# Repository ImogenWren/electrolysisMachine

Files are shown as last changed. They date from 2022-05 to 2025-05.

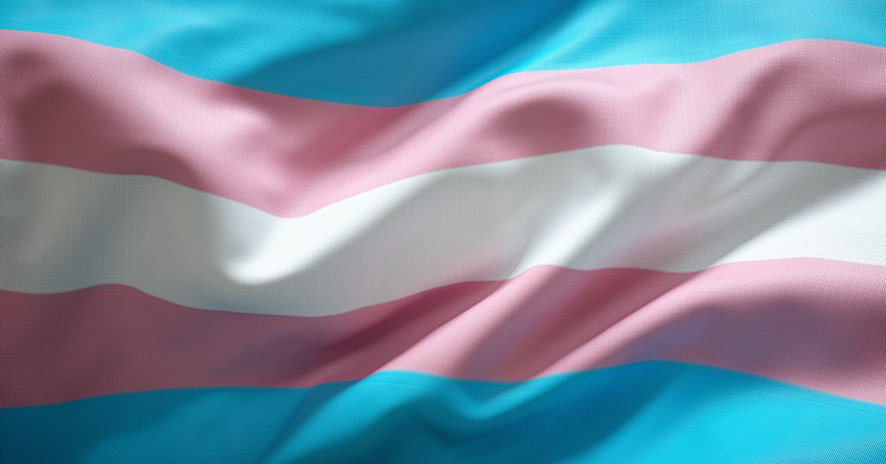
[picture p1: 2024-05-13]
Documentation/TransFlag_AdobeStock_279219643.png

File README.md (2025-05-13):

# electrolysisMachine
 Schematics & Build Plan for DIY Electrolysis Machine for Hair Removal #transhealth

## Contributers
_The following people are thanked for their contribution towards this project_
 - Imogen Wren -> Electronics Lead
 - xxxxxx      -> Power Supply & BMS design

## Notes
_I have just been made aware of someone who is following the origional reddit design, and is quite far into the process with PCBs already in production. Please find a link to this project here: https://hexbear.net/post/2795875_

However I am going to carry on with my design, as I believe my version will be far more useable for those that dont have electronic test equipment to hand.

## System Description
This project is an attempt to build a digitallly controlled version of this DIY Hair Electrolysis machine found on the reddit post [i_built_an_electrolysis_machine_epilator](https://www.reddit.com/r/electronics/comments/8ek9dt/i_built_an_electrolysis_machine_epilator/).
The origional design requires external ampmeters to calibrate, and relies on manually tuning and testing the circuit to ensure settings are correct before delivering current to the hair follical.

To make this project accessable, and build in the ability to add additional safety system, the analog elements should be replaced with digital electronics. The digital electronics should be based around the Arduino Framework to make it as easy as possible for others to build this project.
Once the circuit has been proven, a PCB will be designed to allow others to easy replicate the project.

The hope is to make this a complete open-source, safe, cheap and easy system to build and use, to maximise the impact to the communities that are currently denied access to private hair removal services.

This project is open-source and welcomes collaborators on everything from project goals, design, production and testing!

NOTE: _This is an attempt to design a medical product to deliver current through a paitents skin, within in an open source framework.
Any attempt to follow the designs or guides within this repo are undertaken ENTIRELY at the users own risk._ 

## Design Goals
- [G1] Safe & Consistant operation of a constant current source, able to deliver up to 2.0 mA in pulses of up to 10s between probes attached to users skin.
- [G2] Current Source should be controllable down to 0.0 mA, with a resolution of at least 0.2 mA and accuracy of +-0.2 mA. (Exact values to be reviewed)
- Timer pulse should be controllable down to 1.0 mS, with a resolution of at least 0.5 mS, and accuracy of +-0.2 mS. (Exact values to be reviewed)
- 0-2 mA current to voltage sensor with a resolution of at least 0.2 mA and accuracy of +-0.2 mA (Exact values to be reviewed)
- Operation from 3S or less LiPo battery pack. (Can be reviewed and voltage increased if nessissary to achieve other design goals)
- Battery Management System (BMS) with USB-C (If 5V is sufficient to charge) AND 2.1mm DC jack (or similar generic connector) included.
- Passive Safety system to cut power if 2.0 +-0.2 mA is exceeded.
- Passive safety system to cut power if 10s pulse time is exceeded.
- Microcontroller will be AtMega328p OR Arduino Nano Dev board for ease of replication. 
- Simple to operate user interface:
 - Large display for SET_CURRENT, PULSE_TIME.
 - Settings menu to change MAX_CURRENT, MAX_PULSELENGTH
 - 1x Rotary Encoder with button for user inputs.
 - 1x TRIGGER button
 - 1x CANCEL button
 - Save at least 3x User profiles for quick settings changes
- 3D printable case to contain both electronics, battery system and probes.
- Clear & Simple Build Manual
- Clear & Simple operation instructions (Will need to collaborate to ensure clear communication of medical information)

### Strech Goals
- 3D printable case to include hygenic supplies required for safe operation.
- Chargeable on 5V USB, or 12V power.

## Project Steps:
_These steps are each created with the intent of de-risking the project as quickly as possible,
by focusing on small functional prototypes that can be intergrated at the earliest opportunity,
avoiding increasing complexity untill individual sub-systems are proven._

1. Model voltage controlled, 0-2mA constant current driver in LTspice. [x]
 - 1b. Model Power Supply [x]
2. Construct Current source prototype & Test. [x]
   - 2b. Construct and test power supply. [x]
3. Model 0-2 mA current to 0-5 V sensing circuit in LTspice. []
4. Construct current sensor prototype & test. []
5. Integrate current sensor with Arduino controller and test ability to meet sensitivity requirements. []
6. Integrade constant current driver with Arduino controller, including manual (pot) controls, and test accuracy of output pulse against requirements. [] <br>
- 6b. Create Alpha Version firmware for manual operation of the PULSE_OUTPUT  [] 
7. Model circuit protection concepts in LTspice. []
8. Integrate passive circuit protection to existing prototypes (if possible) and test against requirements.[]
9. Integrate User Interface with existing prototypes and test function of dsiplay & all input devices. []
10. Finalise schematic & Design PCB [] <br>
- 10b. Start design of 3D printed enclosure, to coencide with PCB design (Though should not block PCB design or production) []
11. Develop Beta version firmware including Functional user interface. []
12. Build Production prototype. []
13. Test Beta Firmware with Production prototype. []
14. Release Verified V1.0.0 PCB design & Make PCBs available to purchase. []
15. Release production Firmware. []
16. Develop "DIY Kit" Including build & user guides. []

## Design: Schematic
_The schematic is the most up to date & tested version of each sub system_

### Power Supply
This circuit has been tested with a 12v power supply, driven from a microcontroller. Duty cycle did not affect voltage generated untill the extremes.
Tested using microcontroller for PWM signal, finished version will be driven by 555 timer. <br>

- Use LM317 to regulate to 30v (https://www.homemade-circuits.com/how-to-build-simplest-variable-power/) NOTE: This could maybe be used as current source
- 
- 



<br>
555 Circuit Values:
- R1: 100k
- R2: 1.5k (sets frequency to 48kHz)
- C1: 10n (sets frequency to 48kHz)

Breadboarded & tested, can deliver 2.09 mA @ 32v, unloaded maxV = 45

## December 2024 Research -> Current Controller
- https://forum.arduino.cc/t/precision-current-control-and-measurment/282352
- https://www.allaboutcircuits.com/textbook/semiconductors/chpt-8/voltage-to-current-signal-conversion/

## Circuit 3: Transconductance Amplifier

- Modelled correctly and is even simpler than previous topologies
- Tested & working with 358C Op-Amp

- Layouyt:
- 

- Mrs Signal Layout


## December 2024 Research -> Current Measure:
- https://www.adafruit.com/product/904
  - "A precision amplifier measures the voltage across the 0.1 ohm, 1% sense resistor. Since the amplifier maximum input difference is ±320mV this means it can measure up to ±3.2 Amps. With the internal 12 bit ADC, the resolution at ±3.2A range is 0.8mA. With the internal gain set at the minimum of div8, the max current is ±400mA and the resolution is 0.1mA"
------------------------------------------------------------------------
>
>

# State-of-the-Art

### Description of the Existing Reddit Design

_It's battery powered. epilator circuit runs off 3 9v batteries in series, ammeter and voltmeter run off a separate supply, from a usb battery pack. 
Device delivers a voltage thats adjustable from 6v to 22v. Current sink (at probe) is adjustable from 0mA to 2mA. 
Supply is run through ecg electrode which is placed right next to the site I'm working on. A 555 timer is used to pulse the current sink. 
I'm using professional electrolysis probes, F4 shank stainless steel. Probe housing is made from a d-sub female crimp pin soldered
to a wire and covered with a piece of heat shrink tubing. (F4 size probe fits snug into the socket)._
(abbxrdy, 2018) Accessed: (Reddit 2022)

## Existing System Use Guide

_To adjust current sink, toggle the test switch an turn the current knob, the value is displayed on the ammeter. To use, slide the test switch back. When the probe is inserted, you hit the trigger button and it delivers the current for a specified time. You can see how much it's sinking. If it's sinking less than what it was set for you can increase the voltage to overcome the resistance between the probe and the electrode. The setting that I use is 0.5mA at 15v. This will kill a pubic hair in 10 seconds without much discomfort if the probe is correctly inserted into the hair follicle.
For more information on what size probes to use for what hairs, and how much current to deliver over whatever time period you can search for a "units of lye" chart_

#### Exposure Requirements

_for me, the settings I'm using are 15 volts with 0.5mA sink. This setting treats a pubic hair in 10-15 seconds when needle is placed properly. It just slides right out._

## Needles & Additional Items Required

https://www.texaselectrolysissupply.com/

Ballet brand, f shank, size 4

### Future Improvements for Reddit Version

_second revision of this thing with a lot more safety considerations. The current source will be galvanically isolated from the main supply and have an adjustable current source configurable from 0mA to 2mA and a fixed current sink set at 2mA. The trigger circuit will use an opto isolator and there will be a current monitor on the isolated area that passes it's reading outside through an iso op amp. If the probe sinks more than 2mA the machine will shut down._

# Personal Thoughts and Reflection

## TODO:
- Replace 555 with microcontroller

## Current Schematic
electrolysisMachine_Schematic_source

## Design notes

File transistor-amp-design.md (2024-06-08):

# Transistor Amplifyer Design
Source Used: https://www.circuitbasics.com/transistor-amplifiers/

This is mostly copied verbatium for now, will go through calculations for my own purposes later:

How the circuit works

Our design begins with a look inside the transistor itself.


_In the emitter, there is a ‘hidden’ resistor Re. You can’t measure it with a multimeter, but it’s there. Re has a dynamic value dependent on the collector current Ic such that Re = 25/Ic,
 where Ic is in mA. So if Ic is 10mA, then Re = 2.5Ω. The other important thing to know is that the transistor’s current gain can be approximated as Ic/Ib and is called hfe. Typically, 
50 to 1000 for small transistors. The transistor choice in this design is not an issue; almost any small signal NPN type will be fine._

_For any transistor to work, it needs to be biased. This means that the base is raised or biased 0.6V higher than the emitter.
Besides that, we also need to think about signal headroom and input impedance. 
Any voltage that we set up on the input is going to affect the voltage at the output. 
The voltage at the output is a DC offset, and we want to make this work in our favor. 
The choice of the collector resistor and the current through it will govern this._

_The first assumption is what this circuit will be driving—what output resistance must it have.
We should have an output resistance at least 2x to 5x lower than the next stage. 
So let’s assume the next stage input resistance will be 47k and make our output resistance 10k. 
We do this simply by making R110k (this is a bit of a simplification but is close enough)._

_The next assumption is that we don’t want a distorted output where one of the half-cycles clips.
We want to set the collector voltage of Q1 to be half-way. So if R1 is 10k and the voltage across 
it is 12/2, i.e., 6V, the current through R1 is V/R = 6/10000 = 0.6mA. This is our collector current,
and we can now find re=25/Ic = 42Ω. We will use this later._

_For stability and good biasing, we would like the emitter of Q1 to be at about 1V. This will allow a 
reasonable signal swing at the base of Q1. So to get 1V across R2 knowing the current through it is 0.6mA,
R2 = V/I = 1/0.6 = 1.6k, let’s make it 1k5. This will change the voltage on the emitter slightly so V=IR = 0.6* 1500 = 0.9V._

_Now, the voltage on the base will ALWAYS be 0.6 higher than the emitter, and the current into the emitter will be Icollector/hfe. 
The datasheet for the BC337 shows an hfe of 600. Let’s assume a bit less to be safe, say 200. So Ibase is 0.6/200 =0.003mA.
For stability, we will make the current flowing down the divider chain R3, R4 ten times bigger, i.e., 0.03mA, so the voltage 
across R4 is 0.9 + 0.6 = 1.5 and the current through is 0.03, R4 = V/I = 1.5/0.03 = 50k. We make it a standard value of 47k. 
This slightly changes the current to 1.5/47k = 0.032mA. R3 has 12V on one end and 1.5 on the other. The voltage across it becomes
12-1.5 = 10.5V, and so R3 = V/I = 10.5/0.032 = 328k. Make it a standard value of 330k. R5 has nothing to do with the transistor design. 
It provides a voltage to supply the electret mic (it has an electrostatic capacitor coupled to a small FET inside), and 10k is a usual value._

_Now, how much gain can we expect? The gain will be R1/R2+re = 10k/ 1k5+42 =6.48. This is not that useful, but we can increase this
by AC bypassing R2 with a capacitor C3 leaving only re. The DC conditions remain the same, but the gain is now 1500/42 = 35.
We must make C3 with a value such that its reactance is equal to R2 at our lowest frequency, 40Hz, so C3 = 1/2πfXc = 2.6uF.
Hence, make it 10uF._

_The remaining design is for the input and output capacitors. C1 is easy. The input resistance is a combination of R3 in parallel with
R4 in parallel with
R2+re*hfe, (1k5+42)*200 = 300k._

_It is pretty much just a bit less than R4, say 40k, but it needs to have a capacitive reactance equal to R4 at the lowest 
frequency we intend to amplify. If we choose 40Hz Xc = 1/(2πfC), then C = 1/2πfXc = 0.39uF. In the same way,
C2 = 1/2π40*10k = 0.4uF. Hence, make it 1uF._

_The next step in our design is to add a buffer transistor to increase the output drive capacity to enable a small
(high impedance) speaker. This is called an emitter follower. It has no voltage gain, but it has a much lower output impedance.
We will also provide some DC negative feedback to ‘lock’ the bias of Q1._

The only components that are going to change are R3 and C4; C2 has been replaced with C4. Without C4, there would be a DC offset across the speaker.
We need to know what the impedance of the load is, i.e., the speaker. This simple circuit cannot drive an 8Ω speaker; you would need a power amplifier for that.
Assuming we are using a cell phone earbud at about 100Ω. For a 12V pp swing that would be about 1W, which is pushing it for this simple circuit, 
the emitter follower’s static DC power should be equal to that to result in 100mA in the transistor, which is way beyond its means.
We are going to back off our expectations and allow a maximum of 10mA in Q2. As Q2 emitter is 6-0.6V = 5.4V then R6=5.4/0.01 = 540, 
call it 560Ω. R3 is now no longer connected to 12V, but to 6V, its value becomes (6-1.5)/0.03 = 150K. C4 is now 1/2π40*100 = 25uF.

amplifier_3-1080x877

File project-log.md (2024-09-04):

# project-log: Electrolysis Machine
_Project log showing complete development notes_
## Step 1: Model Voltage Controlled Current Source
- Current Servo, Voltage Controlled Current Source
 Op-Amp-Voltage-Controlled-Current-Source-Circuit-Diagram
"The third requirement is the shunt resistor. Let's stick into 1ohms 2watt resistor. Additional two resistors are required, one for the MOSFET gate resistor and the other one is the feedback resistor. These two are required for reducing the loading effect. However, the drop between these two resistors is negligible.

Now, we need a power source, it is a bench power supply. There are two channels available in the bench power supply. One of them, the first channel is used to provide power to the Circuit and the other one which is the second channel used to provide the variable voltage to control the source current of the circuit. As the control voltage is applied from an external source, both channels need to be in the same potential, thus the ground terminal of the second channel is connected across the first channel ground terminal."

### LTspice modelling
Most linear response found. Will work with 3v3 logic



Increasing voltage to 27 to match origional (3x 9v)
Commands Used:
- `.dc V2 0 5 0.1`
- Now shows almost linear response across the entire control voltage range


Testing current setpoint given change in R3 (sweep from 0R to 10M)
Commands used:
- `.step param R3 list 0R 1R 10R 100R 1K 10k 100k 1000k 10000k`
- `.op`
- Shows constant current through changing load


### Calculating DAC Resolution (10 bit)
- ADC max val = 1023
- Max Current output = 2.36 mA
- Max Current / Max ADC = 0.00231 mA per ADC
- Resolution of 0.002 mA is possible using Arduino ADC, though slight non-liniarity at the lowest control voltage
- MEETS DESIGN GOAL [G2] Resolution of 0.2mA

(Source - [eee-calculator](https://github.com/PanGalacticTech/engineering-calculator-2023)

### Accounting for PWM
As the control voltage from the microcontroller will be PWM, rather than a descrete voltage, this should be added to the simulation. This may not matter, as average current delivered will be the same, however in the origional design the current supplied was constant, not pulsed and I wish to at least attempt to replicate that. A decision can be made later which outcome is better, though this might require testing which will be hard to quantify if I am the only test subject.

### Origional Design modelling PWM control voltage
Arduino nano PWM frequency = 490.2 (this can be changed but why change if not required)
Period = 1/490.2 = 2.04 mS 
Model PWM frequency at 2 mS period, with 50% Duty
Using Commands: 
`.tran 0 1 0 0.1 startup` // DC Transfer for 1 second after startup <br>
`**PULSE(0 5 0 0 0 1m 2m 0)**` // Pulse voltage source <br>
` step param R3 list 0R 1R 10R 100R 1K 10k 100k 1000k 10000k` // step R3 to show constant current regardsless of load <br>

This shows that the output will also be pulsed, the first attempt to remove this pulse will be the addition of a capacitor to the control voltage. Placed after the 100k resistor, this will form a low pass filter, for which the cutoff frequency must be pushed as low as possible to block all but DC.

Selecting 
> capacitor: 1 uF = cutoff_frequency: 1.59 Hz
> capacitor: 10 uF = cutoff_frequency: 0.16 Hz
> 
 Modelling with 1uF capacitor as these are cheaper and easier to source without going to electrolytic.
Using Commands: 
`.tran 0 1 0 0.1 startup` // DC Transfer for 1 second after startup <br>
`**PULSE(0 5 0 0 0 1m 2m 0)**` // Pulse voltage source <br>
` step param R3 list 0R 1R 10R 100R 1K 10k 100k 1000k 10000k` // step R3 to show constant current regardsless of load <br>

Tested with a few different C1 values, nothing showed significant DC smoothing untill 100 uF, shown below:

DC Voltage Ripple:

DC Current Ripple: 1.30 - 1.18 = 12 mA

Next try modelling with smaller value capacitors in paralellel



DC Current Ripple: 1.30 - 1.18 = 12 mA

NO change!
 100uF is likely optimal for this purpose, though introduces a slower current rise & fall time. 

### Testing capacative filter on output of OP-AMP to mosfet
Now lowpass filter with 10k, 

100uF = 0.16 cutoff frequency


Ramp takes over half a second to reach full power, this may assit in reducing pain or shock, or may prolong pain. Certainly will not be suitable for cutting power to probe.



At 1u, ramp up is only 60mS, current ripple of: 1.26 - 1.224 = 0.036mA ripple this is very acceptable. Wave has also been smoothed to sinusoildal. Could this have an effect on pain?


## Step 1b: Model The Power Supply

_The power supply needs to be capable of providing the correct current considering all of the possible loads that a paitents skin could offer._
In order to specify the full requirements for the power supply, we could take data of different peoples skin resistivity, calculate averages, min & max, however. For the first prototypes we will bypass this, and attempt to replicate the power supply used in the origional project. 

This comprised of 3x 9v batteries, or 27v rail-to-rail.

For this implementation we wish to achieve this from a single 12v power supply at most, as these are the most common available. For this we could use a charge pump.

_For previous, failed attempts at specifying the power supply circuit, see the additional file `step-1b-charge-pump-circuits.md`_ <br>

### Attempt 2: 555 based charge pump
_The initial modelling using a charge pump IC with a +18 and -9v output seemed to be a dead end, so next we will try to model a 555 based charge pump with an output of ~+30v_

This next attempt will use this basic building block: <br>

(circuits-diy.com)


https://www.circuits-diy.com/charge-pump-circuit-getting-higher-voltage-from-low-voltage-source/

We could potentially use the microcontroller itself to provide the PWM for the charge pump, this may be explored later, but first we will keep things as simple as possible and model with a 555 timer. For the 555 circuit, I will be adapting a circuit origionally designed for a high voltage SMPS for use with Nixie Tubes, documented here:
https://pangalactictech.com/12v-dc-to-300v-dc-smps/


NE555 Working Voltage: 4.5-16v, fits perfectly with the 12v supply voltage specification.

#### Modelling Charge Pump
_Initial Results Promising_


stable 36v output given 12v input

next test CV frequency sweep - cant set up correctly

Tested at different CV, rise time differed but max V output did not

Then test with varying loads

tested with additionally diode stage and suitable load:


going to try adding one more diode stage

 Peak voltage of ~30v, capable of just over 30mA of current, 

Decreased R8 t0 4k7, increased frequency to 114 KHz

## Simulating pulse in LTspice
_Finally learned to set waveform using frequency & duty cycle_

At duty cycle of:
0.2 = 21.3v output
other duty cycles no difference

but lower input v of 5v = lower output voltage. need additional diode stage or higher PWM voltage
   
### Current of PWM Signal
I decided to check the current required to deliver the simulations shown above, during inrush

- First looking at inrush current:
- -
- ~100 A

- Then looking at each pulse as steady state is reached:
- 
- Still pulling about 2.5 A

This is absolutly not suitable, microcontroller pins can source about 20-40mA at max. For longevity, we wil try and keep it to about 20 mA

- R = V/I
- R = 5/0.020 = 250 ohm
- So lets put a series resistor in the PWM path to limit the current to this value

-Current limited to 18mA BUT Vout now limited to 11.5 v
- 

- So PWm needs to be amplified, simple transistor will do or does this charge pump approach have a fundemental flaw?

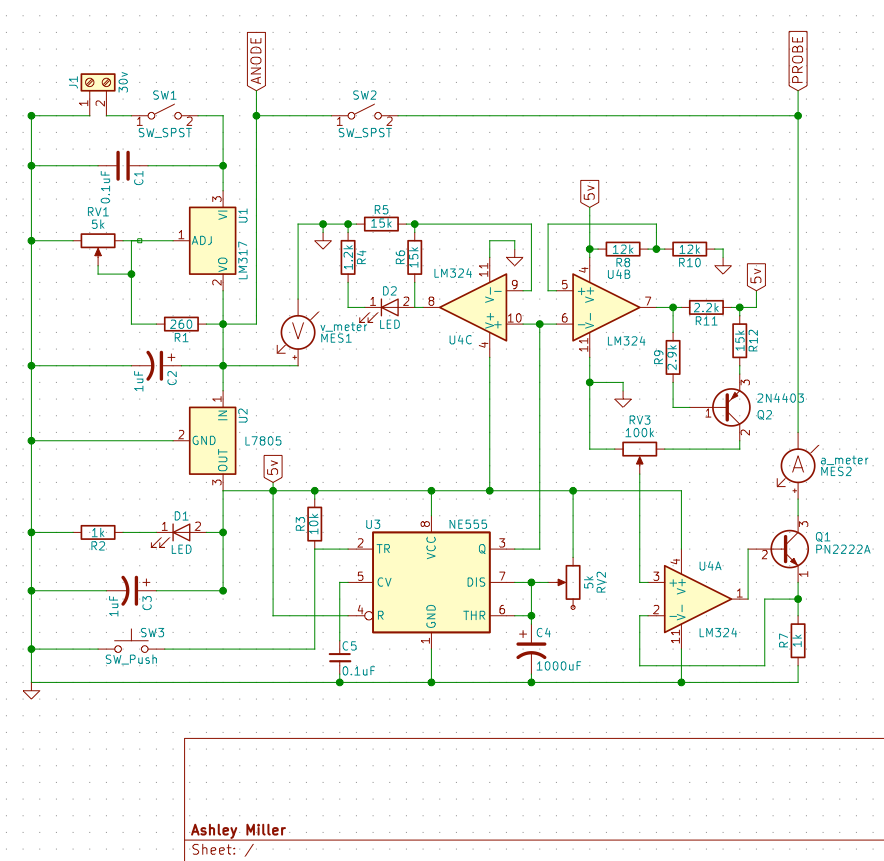
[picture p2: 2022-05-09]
Documentation/electrolysisMachine_Schematic_source.png

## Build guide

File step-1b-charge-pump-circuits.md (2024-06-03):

# Step 1 - Modelling a charge pump circuit
_Moving exploration done on virtual grounds here as it ended up being a dead end in the development tree_

### Attempt 1: Charge Pump IC

The Charge pump selected is based on the Klon charge pump, which delivers a +18v and -9v output, provided a 9v input, and is based on a readily available ILC7660S Charge pump IC. It can also handle voltages up to 12v, given extensive testing (although this may be slightly out of spec and not reccomended) It does offer an opporunity to regulate a 12v input voltage down to 9v to feed the charge pump a very consistant input voltage.

### Schematic


### Issues with Charge Pump
- Unable to model circuit I have experience with as cannot find a model for ILC7660S or TL1044 IC
- In order to get the full 27v rail-to-rail voltage, the negative rail must be used as a virtual ground for the skin probe.
For this reason, I am not going to worry about modelling the charge pump, I know this circuit is cabable of outputting these voltages, however we must ensure that
we can modify the current servo implementation to account for the virtual ground, if this is even possible to do.

## First modelling with -9v virtual ground
- Note: To get this to run needed to use fixed power supply set to +9v, with positive rail grounded

- Showed no current controlability, but current output of ~1.7mA
- After boosting Vsupply to 18v (as if from charge pump) Then current output is able to deliver 2.2mA but still uncontrolled.

## Next trying different groundings (virtual/real)
- Ensure ap-amp is bipolar
- added protection diode to Vcontrol to protect microcontroller from negative voltages

Best option found so far using virtual grounds:



Not great: Controllable down to  ~0.65mA and up to ~1.8mA, must be able to go to 0.0 mA

## Trying to find best feedback resistor.
Used commands: <br>
- `.param Rval=0`
- `.step dec param Rval 0 100k 500` (Logarythmic step Rval
- Put `{Rval` in value to sweep



_Not quite sure what this graph is telling me, trying to expand the range available both up and down._
Immediate conclusions: 
- R1 should be less than 68k to avoid limiting current early.
- Run simulation with lower Vcontrol & compare.
- At Vcontrol = 2.5, current should be ~1.1 mA



- Actual results:
   - For any given feedback resistor value, current is above 1.25
   - Best guess from graph would require a 100k resistor but leaning towards 68k
 
- Arse

- Run again with Vcontrol=0v, should be 0mA
- At 100k, current is still 0.6mA

- I think 68k should be selected, then test R4 step value
- Step change R4 made no difference.
- Setting back to 10k
- try stepping R6 - currently 100k with R5 voltage divider 47r to GND
- INTERESTING RESULT:

### Playing around with voltage divider
_I like using a bigger resistor to GND if possible, so try increasing R6 to reduce control voltage
 
This shows 0.0 mA reached at 220k input resistor. Will set to here then check upper Vcontrol output

max output is now only ~0.55 mA
- Try increasing R5
-  Must be above 120 to prevent limiting current. Very sensitive



## Its nae goood



_Might have to think a little harder about whats happening in the circuit_

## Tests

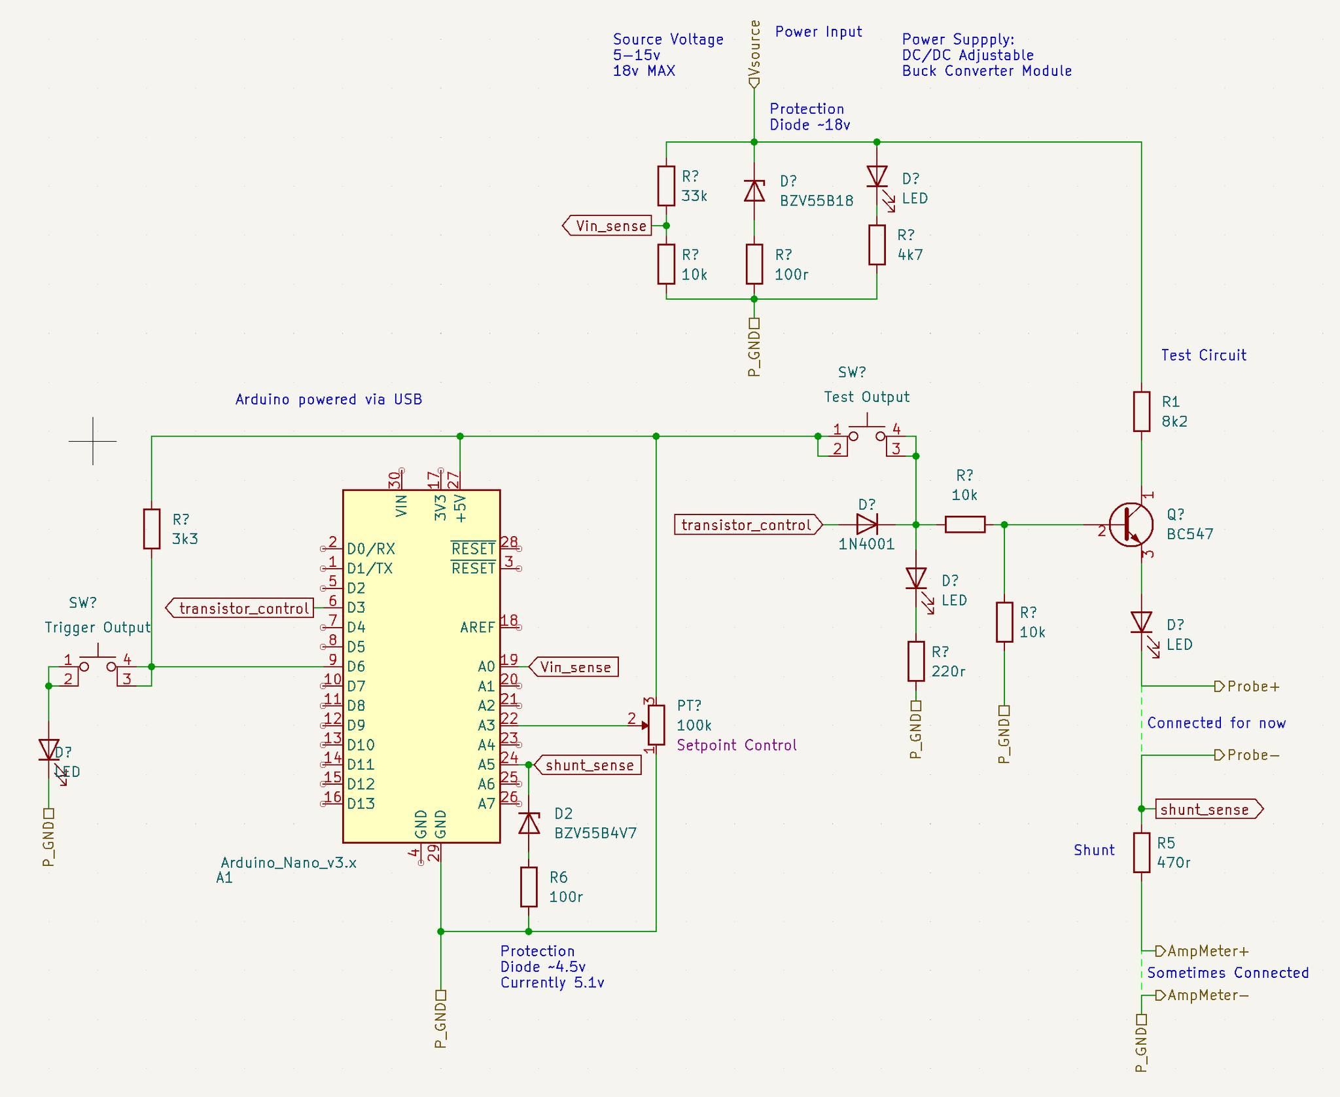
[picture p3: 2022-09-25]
Documentation/Test Circuit Schematic.jpg

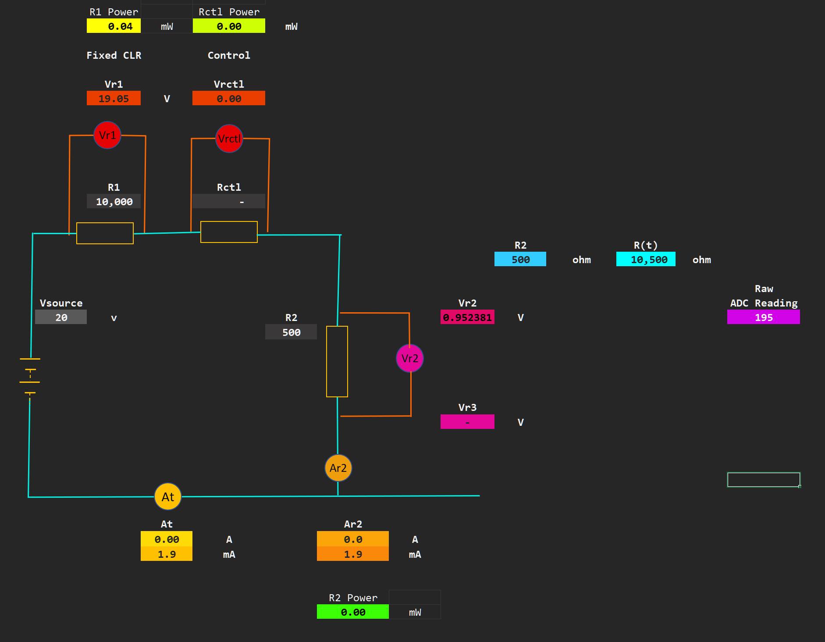
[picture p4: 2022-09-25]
Documentation/Test Circuit Calcs.jpg

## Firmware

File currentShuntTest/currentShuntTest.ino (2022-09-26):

/*
    Test Program for testing current detection using shunt resistor


*/



/* Circuit Specifications:

    Vin <= 20v

    Fixed Resistor = 8k2
    Current Set Resistor = 100-500k
    Shunt Resistor = 500r

    A5 = I measure

    Voltage Divider for Vin Voltage Measurement:
    R1 =  33k
    R2 = 10k

    A7 = Vin Measure


    Circuit Protection:

   15v zener diode with 100r resistor between Vin and GNDs. Clamps Vin to 15v for testing
   5.1v zener diode with 100r resistor between Isense pin and GND. Clamps Detection voltage to <=5v


   Expected Values:

   A5 ADC     =   19    - 195
   A5 Voltage =   0.09  -   0.952
   A5 Current =   0.2   -   1.9

   A7 ADC = 238 - 953
   A7 Voltage = 1.16 - 953
   Vin Voltage = 5 - 20v

*/




#define VIN_SAMPLE_PIN A7
#define SHUNT_SAMPLE_PIN A4

#include <autoDelay.h>
#include <buttonObject.h>



autoDelay sampleDelay;
autoDelay printDelay;
autoDelay inputDelay;
autoDelay outputDelay;

#include "returnStrings.h"


uint16_t u_Vin_ADC;            // Value returned from ACD
float f_Vin_sampled;          // Actual measured voltage
float f_Vin_scaled;           // True Vin Voltage (scaled)


char cs_Vin_sample[20];   // Measured voltage as a char string
char cs_Vin_scaled[20];          // True Scaled voltage as char string

#define ADC_MAX 5.0   // Max voltage for ADC 

#define VIN_ADC_MAX 960
#define VIN_ADC_MIN 0

#define VIN_SAMPLE_MIN 1.16
#define VIN_SAMPLE_MAX 15.0

uint16_t u_shuntADC;               // Value returned from ADC
float f_shunt_Vdrop;            // Measured voltage drop across shunt resistor
float f_shuntI;              // Calculated current through shunt resistor
int16_t shuntI_uA;           // Calculated current in micro amps

#define SHUNT_RESISTOR 500.0   // Shunt resistance in ohms
#define SHUNT_SAMPLE_GAIN 1.0  // gain factor of shunt voltage sampling
#define SHUNT_CURRENT_OFFSET -0.01


char cs_shunt_Vdrop[20];          // Measured voltage drop as char string
char cs_shuntI[20];          // Calculated current as char string


char printBuffer[64];   // buffer to hold all printable values

float voltsPerADC = 0.01;


/* Measured Values & Calibration

    Vin = 5.010   Vin Sampled voltage = 1.18
    Vin = 9.00    Vin Sampled Voltage = 2.065
    Vin = 15.00   Vin Sampled Voltage = 3.448
    15/3.5 = 4.2857
    Therefore
*/

#define VIN_SCALER 4.3
#define VIN_ADC_OFFSET_HIGH -0.20   // offset value between true voltage and calculated voltage at Vmax (15v)
#define VIN_ADC_OFFSET_LOW -0.05      // offset value between true voltage and calculated voltage at Vmin (5v)
float vin_ADV_offset = 0;         // calculated average during setup



/* Adding code for trigger button input
    current set pot input, and
    transistor control output

    At the moment no feedback control, trigger pin sets transistor output high
    Current set pot is read then scaled to mA value but this value is not used yet

*/

#define CONTROL_POT_PIN A0
#define TRIGGER_INPUT_PIN 7
#define TRANSISTOR_OUTPUT_PIN 3
#define INDICATOR_PIN 9   // Mirrors output pin for LED indicator or other indication method
uint16_t controlPotValue;
uint16_t uA_setpoint;

buttonObject button(TRIGGER_INPUT_PIN, BUTTON_PULL_HIGH);    // Set up instance of buttonObject. Pass Button Pin & whether it pulls HIGH, or LOW when pressed.

/*
    PID controller functions

    PID controller will control the current through the shunt resistor using PWM

    pidController library will be used for maths


*/

#include <pidController.h>

#define P_GAIN 1.0
#define I_GAIN 0.0
#define D_GAIN 0.0

pidController PID;

void setupPID() {
  PID.begin();
  PID.updateGain(P_GAIN, I_GAIN, D_GAIN);
}


void setupDigitalPins() {
  pinMode(TRIGGER_INPUT_PIN, INPUT);
  pinMode(TRANSISTOR_OUTPUT_PIN, OUTPUT);
}

void updateOutput(uint8_t output_value) {
  analogWrite(TRANSISTOR_OUTPUT_PIN, output_value);
  analogWrite(INDICATOR_PIN, output_value);    // Mirror output for easy indication
}

void checkButton() {
  //  button.buttonLoop();
  digitalWrite(TRANSISTOR_OUTPUT_PIN, button.detectButton());
}

void controlPot() {
  controlPotValue = analogRead(CONTROL_POT_PIN);   // Sample the ADC
  // This then needs to be scaled to 0 to 2ma. Instead going to scale from 0 to 2000uA to avoid floats
  uA_setpoint = map(controlPotValue, 0, 1024, 0, 2000);
  Serial.print("uA setpoint: ");
  Serial.print(uA_setpoint);
  Serial.print(" uA  |");

}

void setupVinConversions() {
  voltsPerADC = ADC_MAX / 1024.0;
  Serial.print("Volts Per ADC: ");
  Serial.println(voltsPerADC, 6);
  vin_ADV_offset = (VIN_ADC_OFFSET_HIGH + VIN_ADC_OFFSET_LOW) / 2;
  Serial.print("Vin ADC Offset: ");
  Serial.println(vin_ADV_offset, 6);

}

void setupCurrentConversions() {

}


void sampleADCs() {
  u_Vin_ADC = analogRead(VIN_SAMPLE_PIN);
  u_shuntADC = analogRead(SHUNT_SAMPLE_PIN);
  //  Serial.print("Vin ADC: ");
  //  Serial.print(u_Vin_ADC);
  // Serial.print("Shunt ADC: ");
  //Serial.print(u_shuntADC);
}





void calcVin() {
  f_Vin_sampled = u_Vin_ADC * voltsPerADC;
  f_Vin_scaled = (f_Vin_sampled * VIN_SCALER) + vin_ADV_offset;
  //  Serial.print("  Vin Sample: ");
  //  Serial.print(f_Vin_sampled);
  Serial.print("  Vin Scaled: ");
  Serial.print(f_Vin_scaled);
  Serial.print(" |");
}


void calcShunt() {
  f_shunt_Vdrop = u_shuntADC * voltsPerADC;            // Measured voltage drop across shunt resistor
  f_shuntI = ((f_shunt_Vdrop / SHUNT_RESISTOR) * 1000) + SHUNT_CURRENT_OFFSET;
  shuntI_uA = int(f_shuntI * 1000);
  Serial.print(" Shunt Vdrop: ");
  Serial.print(f_shunt_Vdrop);
  Serial.print(" Shunt Current: ");
  Serial.print(f_shuntI);
  Serial.print(" mA, ");
  Serial.print(shuntI_uA);
  Serial.print(" uA");
}



void printOut() {
  // char buffer[64];
  // sprintf(buffer, "%i, %i, %i ,%i, %i, %i", Vin_ADC, Vin_V_Sampled, Vin_Voltage, I_ADC, shunt_Voltage_Drop, I_Current );
}


float testValue = -96.12345;


void setup() {
  Serial.begin(115200);
  setupVinConversions();
  setupDigitalPins();
  setupPID();
}


void loop() {


  // Input Functions
  // Check the PID Controller Settings and State
  if (inputDelay.millisDelay(PID.g_input_delay_mS)) {
    controlPot();
    PID.updateSetpoint(uA_setpoint);
  }

  if (sampleDelay.microsDelay(PID.g_sample_delay_uS)) {
    sampleADCs();
    calcVin();
    calcShunt();
    checkButton();
    PID.updateInput(shuntI_uA);
    Serial.println(" ");
  }
  // Physical Output
  if (outputDelay.microsDelay(PID.g_output_delay_uS)) {
    PID.g_output_value = PID.PIDcontroller(PID.g_setpoint, PID.g_sensor_value, PID.g_output_value);
    //  error_value = PID.g_setpoint - PID.g_sensor_value;
    // average.addDataPoint(error_value);
    // average_error = average.calcMean();
    updateOutput(PID.g_output_value);
  }


 
  //delay(200);

}

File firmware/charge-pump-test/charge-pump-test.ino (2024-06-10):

/* Electrolysis Machine - Charge Pump Driver Test


  Functions:
  - Pot read to PWM duty cycle
  - PWM output to charge pump
  - Voltage meter for output of charge pump


  Circuit:
  - PWM output goes to NOT gate to produce !PWM signal. 
  - PWM & !PWM to 555 Bistable Timer to produce large voltage swing from Vsuppply
  - Charge Pump Circuit driven from 555 output & Vsupply

*/

#define PWM_PUMP_PIN 3
#define POT_PIN A1

#include <autoDelay.h>

autoDelay printDelay;
#define PRINT_DELAY_mS 1000

// Voltmeter Variables
#define VOLTAGE_SENSE_PIN A4
#define V_MAX 30       // Max voltage to measure
#define VMAX_BUFFER 2  // buffer zone to avoid damage
#define V_ADC 5        // Voltage of the ADC
#define R_ONE 10000    // Resistor from Vin
// Next values must be calculated
#define R_TWO 1500                      // Resister to GND calculated by: R_TWO = R_ONE/((V_MAX+VMAX_BUFFER)/V_ADC)
#define ADC_MAX_V 4.8                   // calculated by ADC_MAX_V = (V_MAX+VMAX_BUFFER)/(R_ONE/R_TWO)
#define ADC_TICKS 1024                  // Calculated from 10 bit ADC
#define VOLTMETER_CURRENT_mA 2.67       //mA   // calculated from I = (V_MAX / (R_ONE + R_TWO))*1000
#define ADC_TO_MEAS_V_SCALER 0.00469    // Calculated as    (ADC_MAX_V/ADC_TICKS)
#define ADC_TO_SOURCE_V_SCALER 0.03125  // Calculated as    (ADC_MAX_V/ADC_TICKS)*(R_ONE/R_TWO)
#define MEAS_V_TO_SOURCE_V_SCALER 6.6   // Calculated as (V_meas * (R_ONE/R_TWO))

float V_meas = 1.4;
float V_source = 9.3;


void calculate_voltage_divider() {
}

void sampleVoltage() {
  int adcRead = analogRead(VOLTAGE_SENSE_PIN);
  V_meas = adcRead * ADC_TO_MEAS_V_SCALER;
  V_source = adcRead * ADC_TO_SOURCE_V_SCALER;
}

void setup() {
  Serial.begin(115200);
  Serial.println("\nCharge Pump Test - Prototype\n");
  TCCR1B = TCCR1B & B11111000 | B00000001;  // for PWM frequency of 31372.55 Hz
  pinMode(PWM_PUMP_PIN, OUTPUT);
  analogWrite(PWM_PUMP_PIN, 0);
}

int potRead;
int dutyPercent;
int pwmValue;
int pot_to_pwm() {
  potRead = analogRead(POT_PIN);
  dutyPercent = potRead / 10.23;
  pwmValue = map(dutyPercent, 0, 100, 0, 255);
  return pwmValue;
}

void print_stats() {
  if (printDelay.millisDelay(PRINT_DELAY_mS)) {
    char buffer[128];
    char V_meas_buffer[8];
    char V_source_buffer[8];
    dtostrf(V_meas, 4, 2, V_meas_buffer);
    dtostrf(V_source, 4, 2, V_source_buffer);
    sprintf(buffer, "dutyPercent: %4i, pwmValue: %4i, V_meas: %s, V_source: %s", dutyPercent, pwmValue, V_meas_buffer, V_source_buffer);
    Serial.println(buffer);
  }
}

void loop() {
  sampleVoltage();
  analogWrite(PWM_PUMP_PIN, pot_to_pwm());
  print_stats();
}

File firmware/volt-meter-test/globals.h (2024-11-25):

// Include all external libraries here

#include <autoDelay.h>


autoDelay sampleDelay;
autoDelay reportDelay;

#define SAMPLE_RATE_HZ 10
#define REPORT_RATE_HZ 2

#define REPORT_ACTIVE true

#define NUM_SAMPLES 10

#define SHUNT_RESISTOR 2200

int16_t sample_delay_mS = 1000 / SAMPLE_RATE_HZ;
int16_t report_delay_mS = 1000 / REPORT_RATE_HZ;




float averaged_IP_one;  // averaged samples from ADCs
float averaged_IP_two;

#define V_ONE_FUDGE_FACTOR 0.5
#define V_TWO_FUDGE_FACTOR 0.4
#define I_SHUNT_FUDGE_FACTOR 0.0
#define R_LOAD_FUDGE_FACTOR 0.0

float V_one;    //    = averaged_acd_to_voltage(averaged_IP_one);
float V_two;    //    = averaged_acd_to_voltage(averaged_IP_two);
float V_drop;   //   = V_one - V_two;
float I_shunt;  //  = calculate_I_shunt(V_two, SHUNT_RESISTOR);
int32_t Rload;  //  = calculate_load_resistor(V_drop, I_shunt);

char V_one_buf[8];   // to hold values for printing neatly
char V_two_buf[8];
char V_drop_buf[8];
char I_shunt_buf[8];
char R_load_buf[8];

// Include any local headers here (at bottom of globals.h)
#include "circuitAnalysis.h"
#include "oledFunctions.h"

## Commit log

2022-05-11 Added KiCad Files
    [electrolysisMachine.kicad_pcb, electrolysisMachine.kicad_sch]
2022-05-22 started work on shcematic
    [electrolysisMachine.kicad_sch]
2022-05-23 Schematic Layout Continued
    [electrolysisMachine.kicad_sch]
2022-07-03 Organising schem and added hirarchical sheets
    [electrolysisMachine.kicad_sch, microcontroller.kicad_sch, power_distribution.kicad_sch]
2022-09-17 Added test circuit schematic
    [electrolysisMachine.kicad_sch, microcontroller.kicad_sch]
2022-09-19 Voltage and Current Detection working well
2024-05-14 added PWM circuit analysis
2024-06-04 testing 555 based charge pump
2024-06-08 Looking at current supplied by PWM feed
2024-06-09 using microcontroller for driving charge pump doesnt seem workable
2024-09-01 added model to validate against physical circuit
2024-09-03 added calculator for precision current-pump
2024-09-03 added calculation for 20mA source
2024-09-04 modelled new current pump
2024-09-22 updated kicad schematic
    [electrolysisMachine.kicad_sch, microcontroller.kicad_sch, power_distribution.kicad_sch]
2024-11-22 volt & resistance meter test working in principle
    #TODO Add current sensing
2024-11-24 voltmeter, current meter and resistance meter all working (ish) OLED also installed and functional
2024-11-25 OLED fully functional for multimeter & basic calibration of reported values
2025-01-30 new prototype layouts
